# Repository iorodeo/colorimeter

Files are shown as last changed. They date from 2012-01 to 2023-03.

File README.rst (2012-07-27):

Colorimeter
-----------

Design files, software and firmware for IO Rodeos's open source (hardware &
software) scientific colorimeter kit for educators, students and DIY
scientists. Colorimeters are analytical devices commonly used in science labs to measure
the concentration of a solution from its light absorbing properties.
Colorimeters are extremely useful and flexible lab instruments for a wide range
of science education labs. 

This packages contains:

* Design files for the colorimeter Electronic Kicad) and Mechanical (py2scad) components.

* Arduino firmware and Python serial library for communicating the colorimeter.  

* A suite of software (w/GUI) for taking measurements with the colorimeter - e.g. 
  measuring transmittance and absorbance, generating standard curves, and  measuring 
  the concentration of solutions.

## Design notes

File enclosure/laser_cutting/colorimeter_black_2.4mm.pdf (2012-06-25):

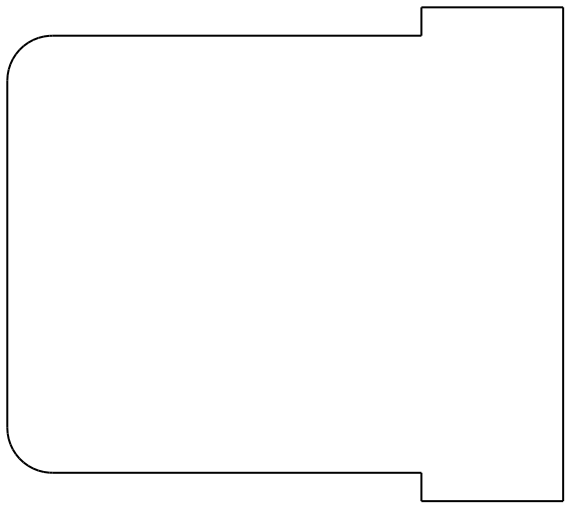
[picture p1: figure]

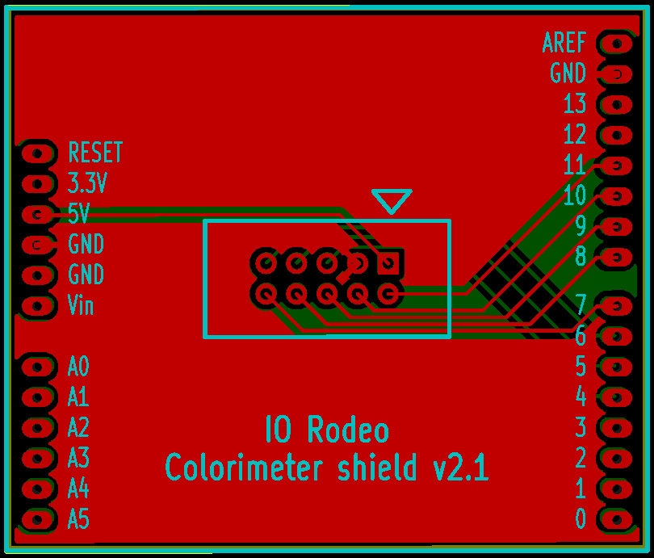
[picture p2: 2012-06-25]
kicad_design/colorimeter_shield/gerber_shield_v2p1/colorimeter_shield.png

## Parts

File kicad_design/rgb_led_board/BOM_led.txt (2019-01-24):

part        decription                        vendor      PN                               QTY
----------------------------------------------------------------------------------------------------
U1          SMT RGB LED                       Digikey    475-2822-1-ND or 475-3547-1-ND     1
P1          4 pin SMT male header             Digikey    S1013E-04-ND                       1
R1, R2      SMT resistor 90 ohm               Digikey    P90.9CCT-ND                        2
R3          SMT resistor 150 ohm              Digikey    P150CCT-ND                         1

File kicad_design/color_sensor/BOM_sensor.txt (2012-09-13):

part     decription                        vendor   PN                  QTY
----------------------------------------------------------------------------------
U1      SMT Color sensor	               Mouser	856-TCS3200D-TR       1
P2      4 pin SMT male header              Digikey	S1013E-04-ND          1
C1      SMT 0.1uF capacitor	               Digikey	490-1577-1-ND         1
P1      5x2 shrouded header	               Digikey	S9169-ND              1

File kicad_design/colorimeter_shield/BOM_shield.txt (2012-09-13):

part     decription                        vendor   PN                  QTY
----------------------------------------------------------------------------------
P1       5x2 shrouded header	           Digikey	S9169-ND             1
P2       0.1" breakaway male pin header    Digikey  SAM1031-30-ND        1

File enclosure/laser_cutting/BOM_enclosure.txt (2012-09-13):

QTY      decription                          vendor          PN                  
------------------------------------------------------------------------
4        4-40 hex standoffs 1 ¾” long        McMaster-Carr   91780A038
2        4-40 hex standoffs 1 ¼” long        McMaster-Carr   91780A034
16       4-40 machine screws 3/8” long       McMaster-Carr   91249A108
4        4-40 machine screws 1/2" long       McMaster-Carr   91249A111
8        4-40 machine screw nuts             McMaster-Carr   96537A120
4        3” female-female wire               Pololu          1806
2        connector housing                   Pololu          1903

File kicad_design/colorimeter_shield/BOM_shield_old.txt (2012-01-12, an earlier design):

part     decription                        vendor   PN                  QTY
----------------------------------------------------------------------------------
C1       SMT 10uF Capacitor 	           Digikey	493-2886-1-ND        1
P1       4x1 connector – friction lock	   Digikey	A1922-ND             1
P2       5x2 shrouded header	           Digikey	S9169-ND             1
P4       2-pin connector		
K1       3-pin connector		
SW1      SMT switch	                       Digikey	CKN10223CT-ND        1
RV1      Potentiometer	                   Digikey	CT2264-ND            1
SHIELD1  Arduino Stackable Header Kit 	   Sparkfun	PRT-10007            1

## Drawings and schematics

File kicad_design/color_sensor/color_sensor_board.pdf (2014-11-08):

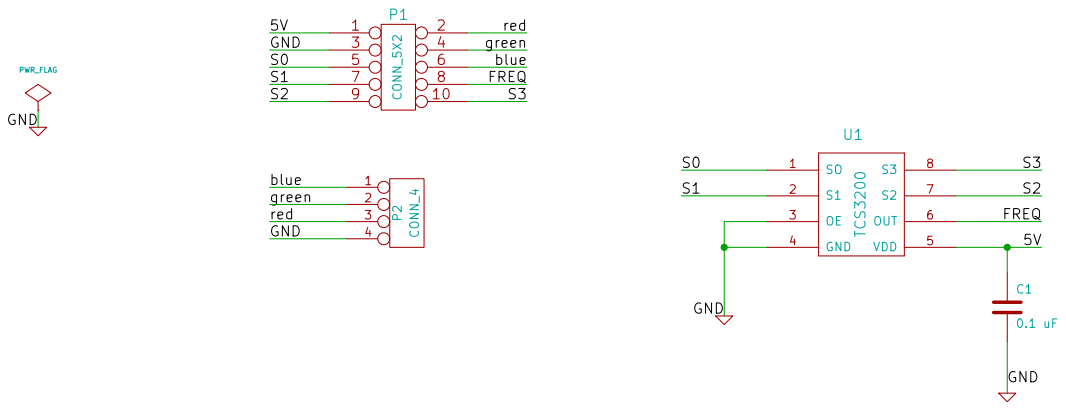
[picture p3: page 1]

Id: 1/1 Title: File: color_sensor_board.sch
Sheet: /

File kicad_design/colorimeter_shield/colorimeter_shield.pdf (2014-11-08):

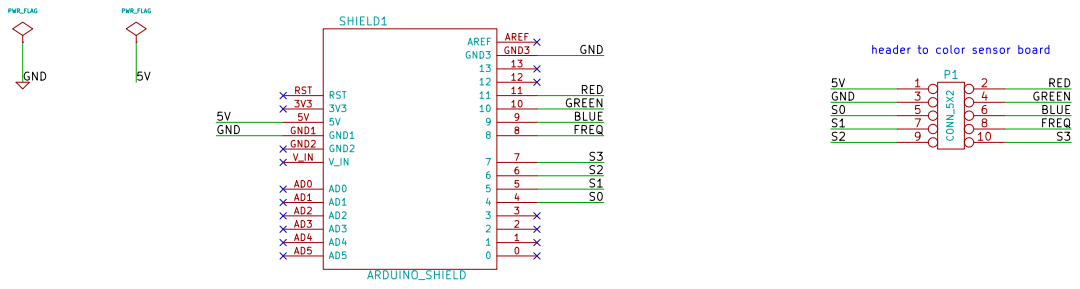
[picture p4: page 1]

9 BLUE
8 | FREQ

Id: 1/1 Title: File: colorimeter_shield.sch
Sheet: /

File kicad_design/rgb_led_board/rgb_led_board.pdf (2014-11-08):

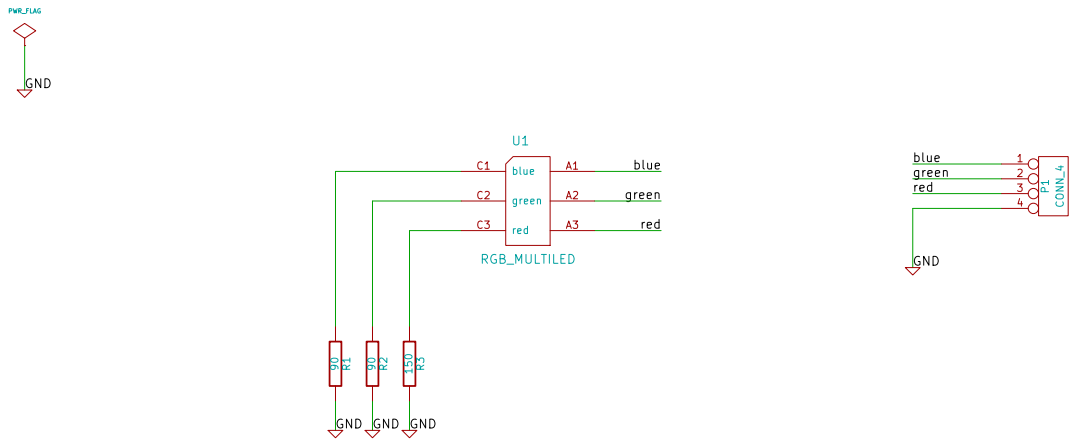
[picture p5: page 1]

Id: 1/1 Title: File: rgb_led_board.sch
Sheet: /

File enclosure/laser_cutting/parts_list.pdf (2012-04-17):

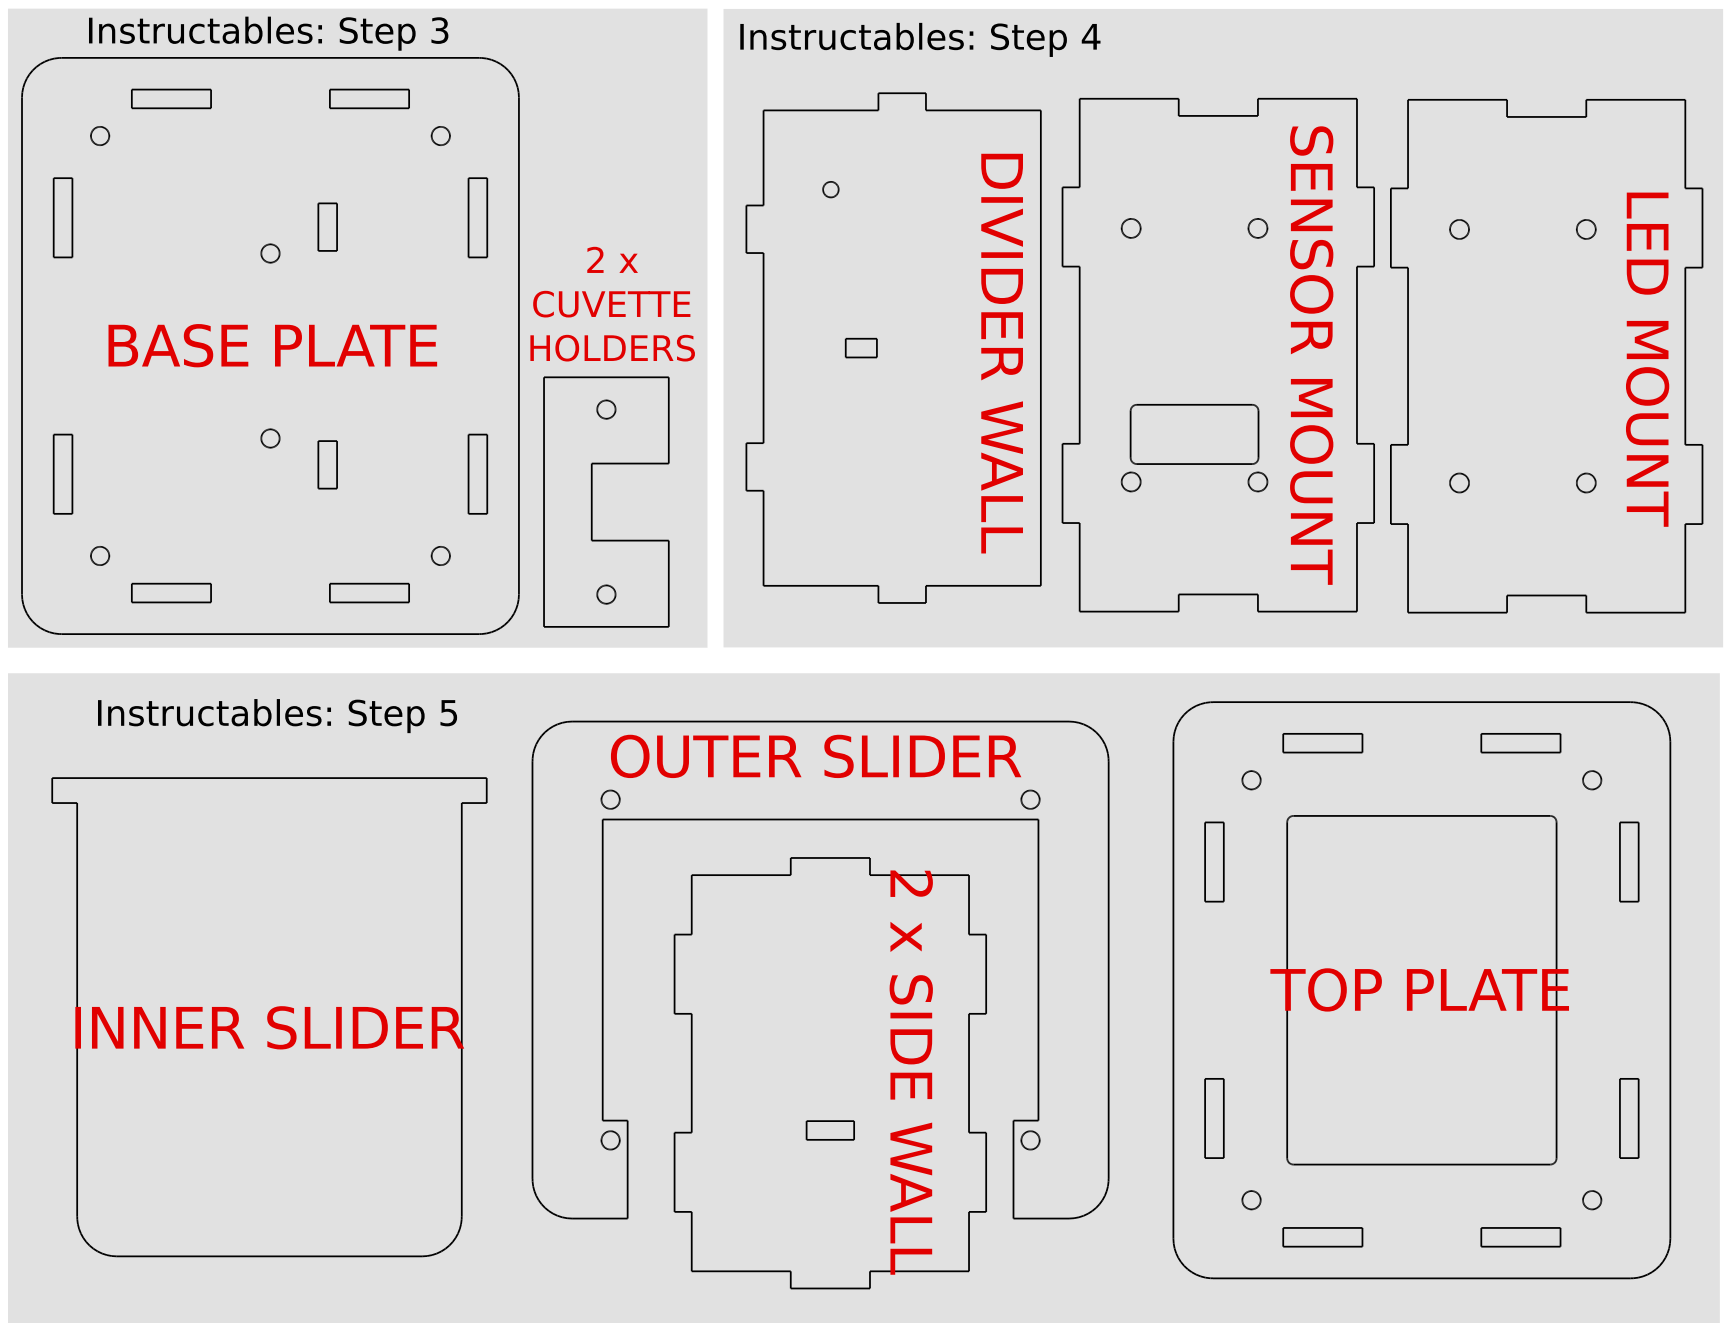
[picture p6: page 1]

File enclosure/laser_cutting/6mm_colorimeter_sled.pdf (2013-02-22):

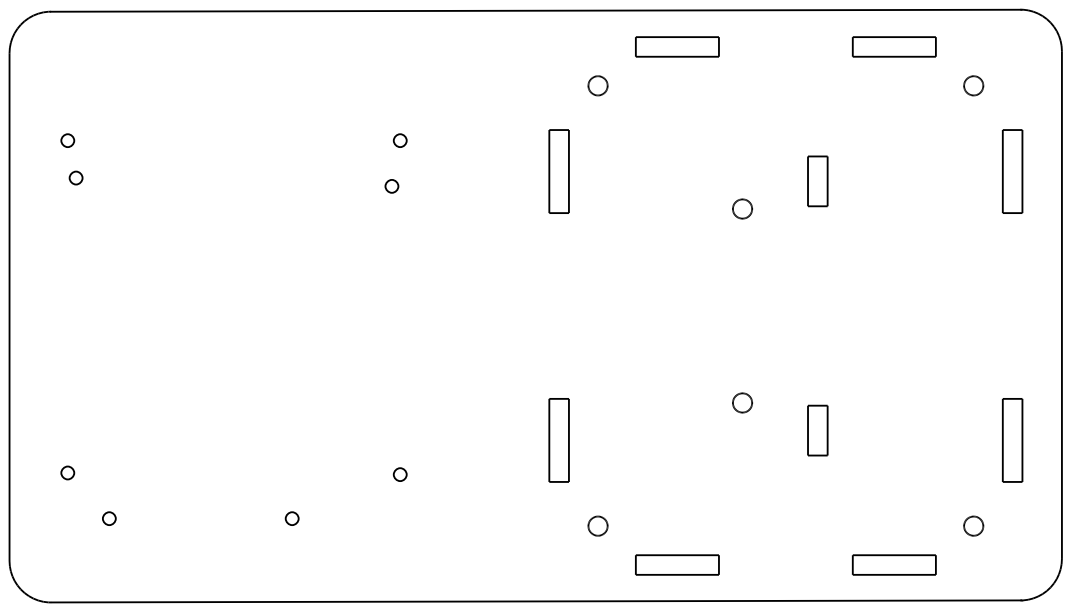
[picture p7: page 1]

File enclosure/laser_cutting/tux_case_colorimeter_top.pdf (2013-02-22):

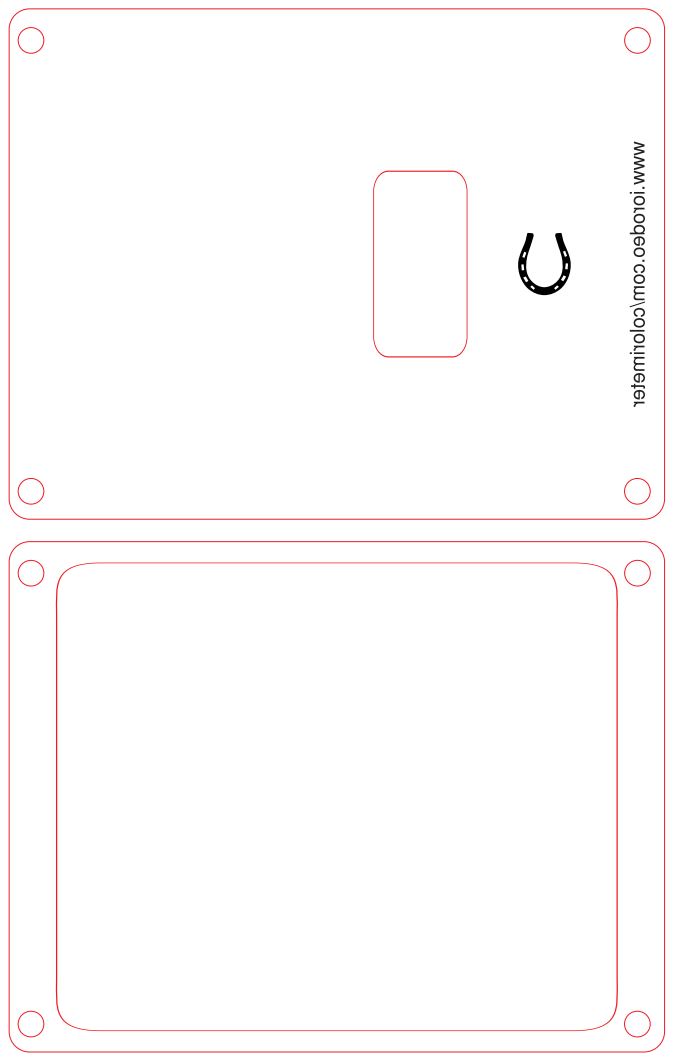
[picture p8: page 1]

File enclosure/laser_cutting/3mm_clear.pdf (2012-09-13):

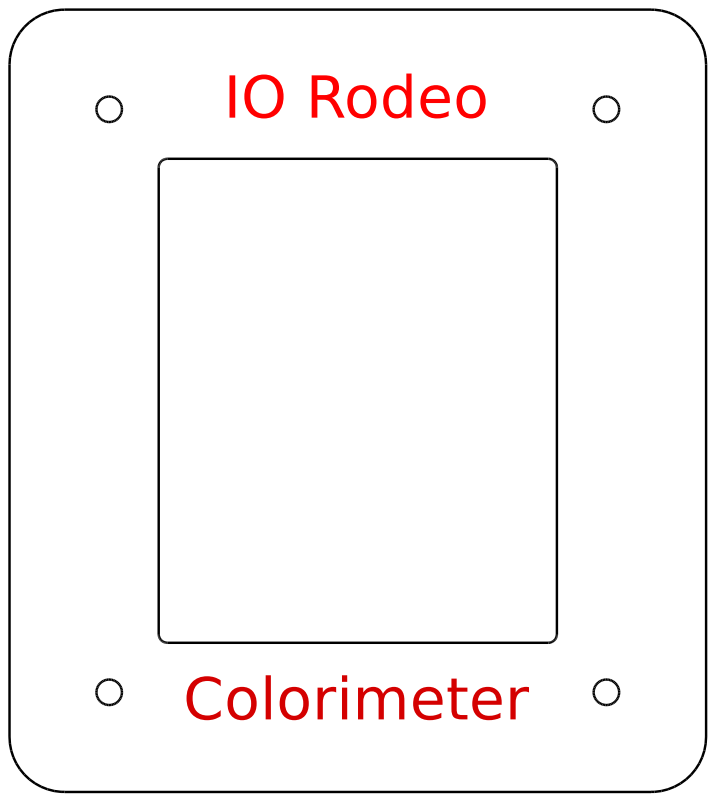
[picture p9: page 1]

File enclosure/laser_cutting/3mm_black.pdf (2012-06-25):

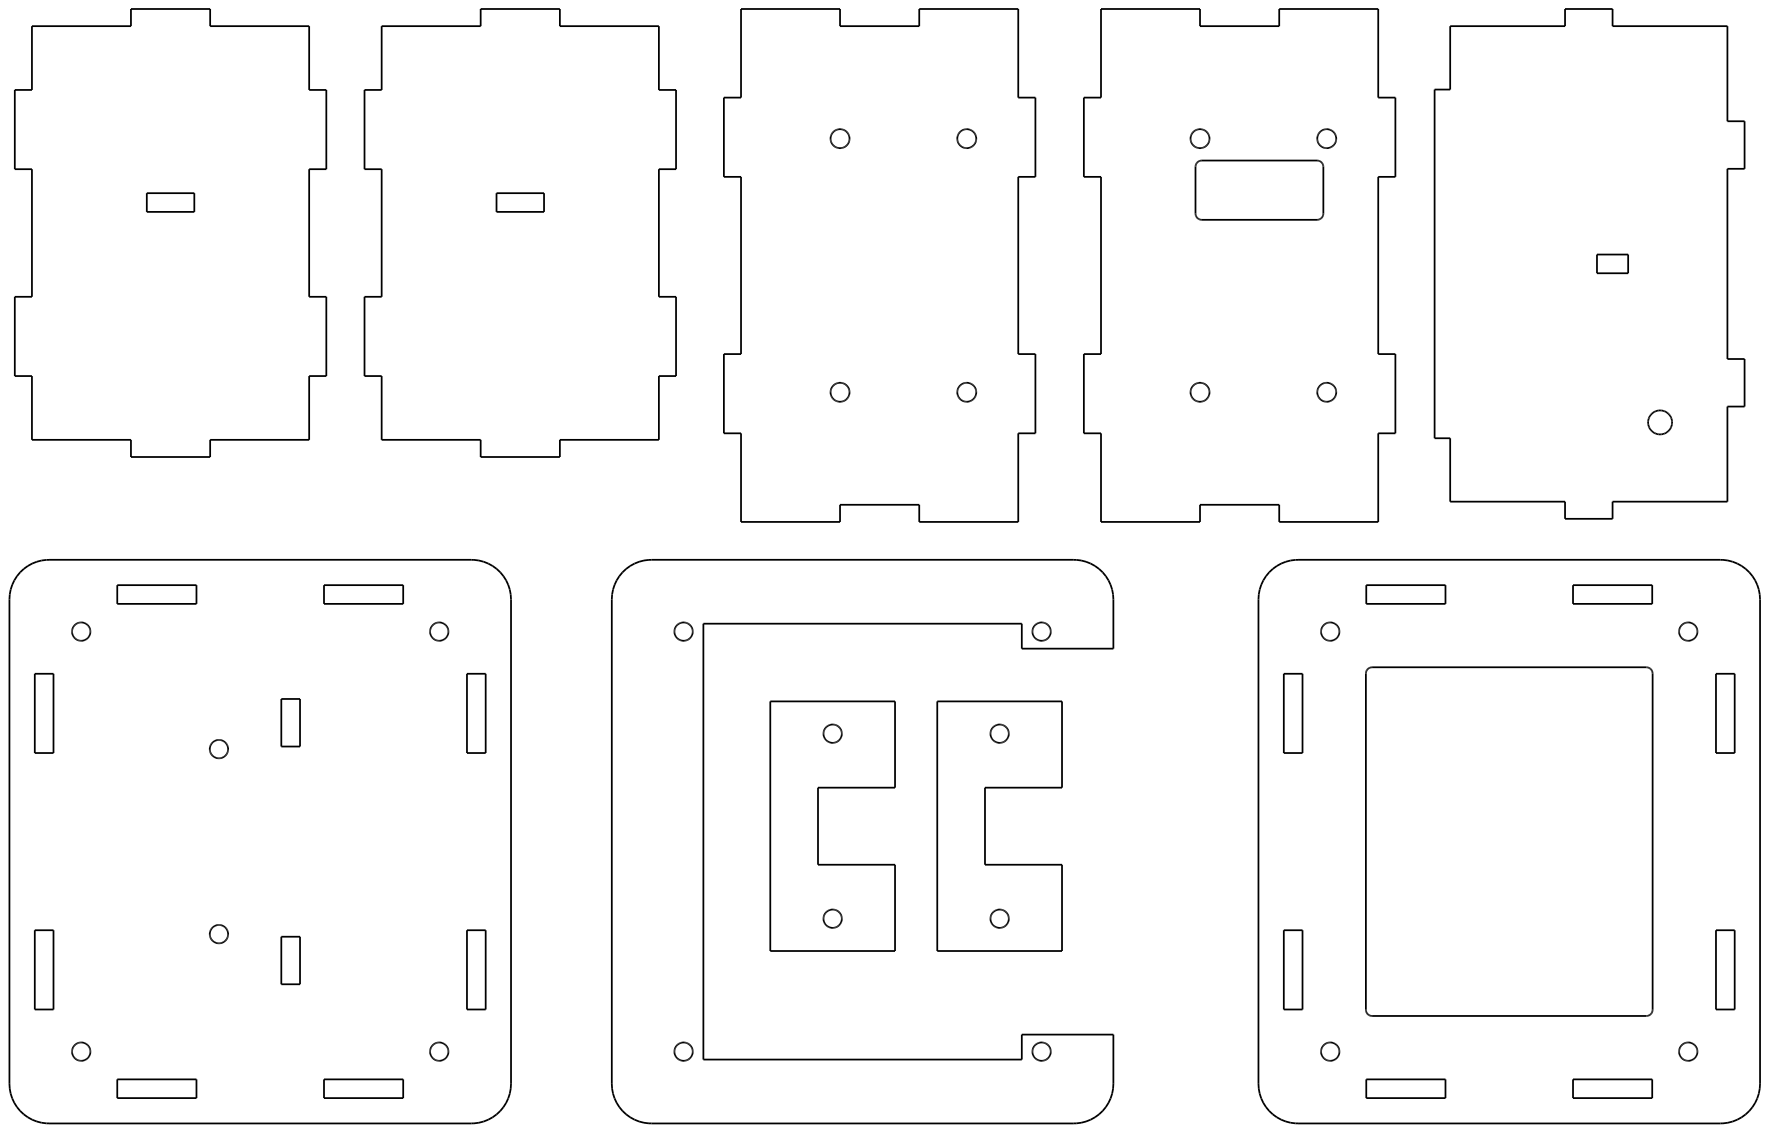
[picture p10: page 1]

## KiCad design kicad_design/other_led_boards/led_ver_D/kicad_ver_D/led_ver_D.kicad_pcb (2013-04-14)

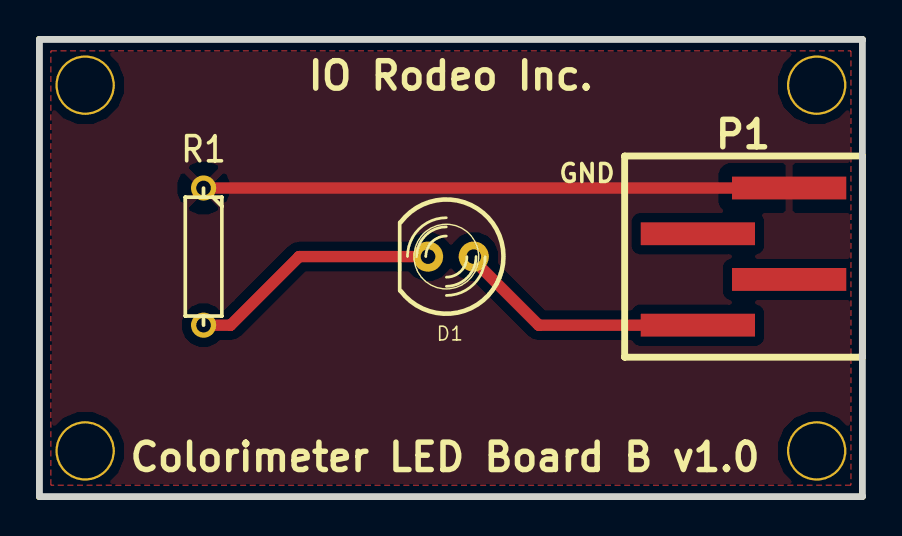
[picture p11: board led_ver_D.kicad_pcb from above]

Board: 2 copper layers, 45.7 x 25.4 mm, 7 parts (0 on the bottom side), 3 nets.

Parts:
D1: LED; LED-5MM
M1, M2, M3, M4: MOUNT_HOLE_4_40
P1: CONN_4; smt
R1: 40; R3

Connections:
/Blue: D1.1, P1.1
GND: P1.4, R1.1
unnamed: D1.2, R1.2

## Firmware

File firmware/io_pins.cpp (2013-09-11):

#include "io_pins.h"
#if defined(ARDUINO) && ARDUINO >= 100
#include "Arduino.h"
#else
#include "WProgram.h"
#endif

#ifndef BLE_SHIELD

// IO Pins for UNO Shield 
// --------------------------------------------------------

// RGB LED Control Pins
const int LED_BLU_PIN = 9; 
const int LED_GRN_PIN = 10; 
const int LED_RED_PIN = 11;

// Color Sensor Control Pins
const int COLOR_SENSOR_S0 = 4; 
const int COLOR_SENSOR_S1 = 5; 
const int COLOR_SENSOR_S2 = 6; 
const int COLOR_SENSOR_S3 = 7; 
const int COLOR_SENSOR_FO = 8;       

#else

// IO Pins for BLE shield
// --------------------------------------------------------

// RGB LED Control Pins
const int LED_BLU_PIN = 3; 
const int LED_GRN_PIN = A1; 
const int LED_RED_PIN = A0;

// Color Sensor Control Pins
const int COLOR_SENSOR_S0 = 4; 
const int COLOR_SENSOR_S1 = 5; 
const int COLOR_SENSOR_S2 = 6; 
const int COLOR_SENSOR_S3 = 7; 
const int COLOR_SENSOR_FO = 2;       

#endif

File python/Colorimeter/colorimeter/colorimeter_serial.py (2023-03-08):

from __future__ import print_function
import serial
import time

RESET_SLEEP_T = 2.0

CMD_CALIBRATE = 0
CMD_GET_MEASUREMENT = 1
CMD_SET_NUM_SAMPLES = 2
CMD_GET_NUM_SAMPLES = 3
CMD_GET_CALIBRATION = 4

CMD_CALIBRATE_RED = 5 
CMD_CALIBRATE_GREEN = 6
CMD_CALIBRATE_BLUE = 7
CMD_CALIBRATE_WHITE = 8

CMD_GET_MEASUREMENT_RED = 9
CMD_GET_MEASUREMENT_GREEN = 10
CMD_GET_MEASUREMENT_BLUE = 11
CMD_GET_MEASUREMENT_WHITE = 12

CMD_SET_MODE_COLOR_SPECIFIC = 13
CMD_SET_MODE_COLOR_INDEPENDENT = 14
CMD_GET_SENSOR_MODE = 15

SENSOR_MODE_COLOR_SPECIFIC = 0
SENSOR_MODE_COLOR_INDEPENDENT = 1

LED_COLOR_LIST = 'red', 'green', 'blue', 'white'

RSP_ERROR = 0
RSP_SUCCESS = 1

class Colorimeter(serial.Serial):

    def __init__(self, port, timeout=10.0, debug=False):
        params = {'baudrate': 9600, 'timeout': timeout}
        super(Colorimeter,self).__init__(port,**params)
        time.sleep(RESET_SLEEP_T)
        self.debug=debug
        self.clearBuffer()

    def clearBuffer(self):
        time.sleep(0.1)
        while self.inWaiting() > 0:
            self.read(self.inWaiting())
            time.sleep(0.1)

    def sendCmd(self,cmd):
        """
        Send command to colorimeter and receiver response.
        """
        self.write('{0}\n'.format(cmd).encode())
        rsp = self.readline()
        self.clearBuffer()
        if self.debug:
            print('cmd: ', cmd)
            print('rsp: ', rsp)

        if len(rsp) < 2:
            raise IOError('response from device is too short')

        if rsp[1] == str(RSP_ERROR):
            raise IOError('RSP_ERROR: {0}'.format(rsp))

        try:
            rsp = eval(rsp.strip())
        except Exception:
            raise IOError('bad response unable to parse result')

        return rsp
        
    def calibrate(self,color=None):
        """
        Calibrate the colorimeter (all channels).
        """
        if color is None:
            cmd = '[{0}]'.format(CMD_CALIBRATE) 
            rsp = self.sendCmd(cmd)
        else:
            color = color.lower()
            if not color in LED_COLOR_LIST:
                raise ValueError('unknown device color {0}'.format(color))
            calFunc = getattr(self,'calibrate{0}'.format(color.title()))
            rsp = calFunc()

    def calibrateRed(self):
        """
        Calibrate the red channel of the colorimeter
        """
        cmd = '[{0}]'.format(CMD_CALIBRATE_RED)
        rsp = self.sendCmd(cmd)

    def calibrateGreen(self):
        """
        Calibrate the green channel of the colorimeter
        """
        cmd = '[{0}]'.format(CMD_CALIBRATE_GREEN)
        rsp = self.sendCmd(cmd)

    def calibrateBlue(self):
        """
        Calibrate the blue channe of the colorimeter
        """
        cmd = '[{0}]'.format(CMD_CALIBRATE_BLUE)
        rsp = self.sendCmd(cmd)

    def calibrateWhite(self):
        """
        Calibrate the white channel of the colorimeter
        """
        cmd = '[{0}]'.format(CMD_CALIBRATE_WHITE)
        rsp = self.sendCmd(cmd)

    def getCalibration(self):
        """
        Get the current calibration freqeuncy values.

        Returns the calibration freqeuncies for red, green, blue and white
        light.
        """
        cmd = '[{0}]'.format(CMD_GET_CALIBRATION)
        rsp = self.sendCmd(cmd)
        return rsp[1:5] 

    def getMeasurement(self,color='all'):
        """
        Get a measurement from the device. 
        """
        if color == 'all':
            cmd = '[{0}]'.format(CMD_GET_MEASUREMENT)
            rsp = self.sendCmd(cmd)
            freq = tuple(rsp[1:5])
            tran = tuple(rsp[5:9])
            abso = tuple(rsp[9:])
        elif color in ('red', 'green', 'blue', 'white'):
            measureFunc = getattr(self,'getMeasurement{0}'.format(color.title()))
            freq, tran, abso = measureFunc()
        else:
            raise ValueError('unknown color {0}'.format(color))
        return freq, tran, abso

    def getMeasurementRed(self):
        """
        Get a measurement from the red channel
        """
        cmd = '[{0}]'.format(CMD_GET_MEASUREMENT_RED)
        rsp = self.sendCmd(cmd)
        freq, tran, abso = rsp[1:4]
        return freq, tran, abso

    def getMeasurementGreen(self):
        """
        Get a measurement from the green channel
        """
        cmd = '[{0}]'.format(CMD_GET_MEASUREMENT_GREEN)
        rsp = self.sendCmd(cmd)
        freq, tran, abso = rsp[1:4]
        return freq, tran, abso

    def getMeasurementBlue(self):
        """
        Get a measurement from the blue channel
        """
        cmd = '[{0}]'.format(CMD_GET_MEASUREMENT_BLUE)
        rsp = self.sendCmd(cmd)
        freq, tran, abso = rsp[1:4]
        return freq, tran, abso

    def getMeasurementWhite(self):
        """
        Get a measurement from the white channel
        """
        cmd = '[{0}]'.format(CMD_GET_MEASUREMENT_WHITE)
        rsp = self.sendCmd(cmd)
        freq, tran, abso = rsp[1:4]
        return freq, tran, abso

    def setNumSamples(self,value):
        """
        Set the number of samples aquired per measurement.
        """
        if value <= 0 or value > (2**16-1):
            raise ValueError('numSamples must be > 0 or < 2**16 -1')
        cmd = '[{0}, {1}]'.format(CMD_SET_NUM_SAMPLES,value)
        rsp = self.sendCmd(cmd)

    def getNumSamples(self):
        """
        Get the current value set for the number of samples per measurement.
        """
        cmd = '[{0}]'.format(CMD_GET_NUM_SAMPLES) 
        rsp = self.sendCmd(cmd)
        numSamples = rsp[1]
        return numSamples

    def setSensorModeColorSpecific(self):
        """
        Set the sensor to color specific mode. In this mode it will use the 
        red/green/blue/clear color channel of the sensor when using the 
        red/green/blue/white led.
        """
        cmd = '[{0}]'.format(CMD_SET_MODE_COLOR_SPECIFIC)
        rsp = self.sendCmd(cmd)

    def setSensorModeColorIndependent(self):
        """
        Set the sensor to color independent mode. In this mode the clear
        (unfiltered) channel of the light sensor is used regardless of the led
        selected.
        """
        cmd = '[{0}]'.format(CMD_SET_MODE_COLOR_INDEPENDENT)
        rsp = self.sendCmd(cmd)

    def getSensorMode(self):
        """
        Returns the current color sensor mode setting.
        """
        cmd = '[{0}]'.format(CMD_GET_SENSOR_MODE)
        rsp = self.sendCmd(cmd)
        sensorMode = rsp[1]
        return sensorMode

    def printMeasurement(self):
        """
        Test function. Gets a measurement and pretty prints it.
        """
        f, t, a = self.getMeasurement()

        print('Frequency:')
        print('  red:    {0:1.2f}'.format(f[0]))
        print('  green:  {0:1.2f}'.format(f[1]))
        print('  blue:   {0:1.2f}'.format(f[2]))
        print('  white:  {0:1.2f}'.format(f[3]))

        print('Transmission:')
        print('  red:    {0:1.2f}'.format(t[0]))
        print('  green:  {0:1.2f}'.format(t[1]))
        print('  blue:   {0:1.2f}'.format(t[2]))
        print('  white:  {0:1.2f}'.format(t[3]))

        print('Absorbance:')
        print('  red:    {0:1.2f}'.format(a[0]))
        print('  green:  {0:1.2f}'.format(a[1]))
        print('  blue:   {0:1.2f}'.format(a[2]))
        print('  white:  {0:1.2f}'.format(a[3]))

# -----------------------------------------------------------------------------
if __name__ == '__main__':

    dev = Colorimeter('/dev/ttyACM0')
    dev.printMeasurement()







    
        

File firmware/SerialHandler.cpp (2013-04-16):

#if defined(ARDUINO) && ARDUINO >= 100
#include "Arduino.h"
#else
#include "WProgram.h"
#endif
#include "SerialHandler.h"
#include "Streaming.h"

// Constants
// ----------------------------------------------------------------------------
const int CMD_CALIBRATE=0;
const int CMD_GET_MEASUREMENT=1;
const int CMD_SET_NUM_SAMPLES=2;
const int CMD_GET_NUM_SAMPLES=3;
const int CMD_GET_CALIBRATION=4;

const int CMD_CALIBRATE_RED=5;
const int CMD_CALIBRATE_GREEN=6;
const int CMD_CALIBRATE_BLUE=7;
const int CMD_CALIBRATE_WHITE=8;

const int CMD_GET_MEASUREMENT_RED=9;
const int CMD_GET_MEASUREMENT_GREEN=10;
const int CMD_GET_MEASUREMENT_BLUE=11;
const int CMD_GET_MEASUREMENT_WHITE=12;

const int CMD_SET_MODE_COLOR_SPECIFIC=13;
const int CMD_SET_MODE_COLOR_INDEPENDENT=14;
const int CMD_GET_SENSOR_MODE = 15;

const int RSP_ERROR = 0;
const int RSP_SUCCESS = 1;

const uint8_t DBL_STR_LEN = 30;
const uint8_t DBL_PREC = 12;



// Methods
// ----------------------------------------------------------------------------
void SerialHandler::processInput() { 
    while (Serial.available() > 0) {
        process(Serial.read());
        if (messageReady()) {
            switchYard();
            reset();
        }
    }
}

void SerialHandler::switchYard() { 
    uint8_t cmdId;

    cmdId = readInt(0); 

    switch (cmdId) {

        case CMD_CALIBRATE:
            calibrate();
            break;

        case CMD_GET_MEASUREMENT:
            sendMeasurement();
            break;

        case CMD_SET_NUM_SAMPLES:
            setNumSamples();
            break;

        case CMD_GET_NUM_SAMPLES:
            sendNumSamples();
            break;

        case CMD_GET_CALIBRATION:
            sendCalibration();
            break;

        case CMD_CALIBRATE_RED:
            calibrateRed();
            break;

        case CMD_CALIBRATE_GREEN:
            calibrateGreen();
            break;

        case CMD_CALIBRATE_BLUE:
            calibrateBlue();
            break;

        case CMD_CALIBRATE_WHITE:
            calibrateWhite();
            break;

        case CMD_GET_MEASUREMENT_RED:
            sendMeasurementRed();
            break;

        case CMD_GET_MEASUREMENT_GREEN:
            sendMeasurementGreen();
            break;

        case CMD_GET_MEASUREMENT_BLUE:
            sendMeasurementBlue();
            break;

        case CMD_GET_MEASUREMENT_WHITE:
            sendMeasurementWhite();
            break;

        case CMD_SET_MODE_COLOR_SPECIFIC:
            setModeColorSpecific();
            break;

        case CMD_SET_MODE_COLOR_INDEPENDENT:
            setModeColorIndependent();
            break;

        case CMD_GET_SENSOR_MODE:
            sendSensorMode();
            break;

        default:
            unknownCmd();
            break;
    }
}

void SerialHandler::calibrate() { 
    colorimeter.calibrate();
    if (colorimeter.checkCalibration() ) {
        colorimeter.EEPROM_saveCalibration();
        Serial << '[' << RSP_SUCCESS << ']' << endl;
    } 
    else {
        Serial << '[' << RSP_ERROR; 
        Serial << ',' << "calibration failed";
        Serial << ']' << endl;
    }
}

void SerialHandler::calibrateRed() {
    colorimeter.calibrateRed();
    if (colorimeter.checkCalibrationRed()) {
        colorimeter.EEPROM_saveCalibrationRed();
        Serial << '[' << RSP_SUCCESS << ']' << endl;
    }
    else {
        Serial << '[' << RSP_ERROR; 
        Serial << ',' << "calibration failed";
        Serial << ']' << endl;
    }
}

void SerialHandler::calibrateGreen() {
    colorimeter.calibrateGreen();
    if (colorimeter.checkCalibrationGreen()) {
        colorimeter.EEPROM_saveCalibrationGreen();
        Serial << '[' << RSP_SUCCESS << ']' << endl;
    }
    else {
        Serial << '[' << RSP_ERROR; 
        Serial << ',' << "calibration failed";
        Serial << ']' << endl;
    }
}

void SerialHandler::calibrateBlue() {
    colorimeter.calibrateBlue();
    if (colorimeter.checkCalibrationBlue()) {
        colorimeter.EEPROM_saveCalibrationBlue();
        Serial << '[' << RSP_SUCCESS << ']' << endl;
    }
    else {
        Serial << '[' << RSP_ERROR; 
        Serial << ',' << "calibration failed";
        Serial << ']' << endl;
    }
}

void SerialHandler::calibrateWhite() {
    colorimeter.calibrateWhite();
    if (colorimeter.checkCalibrationWhite()) {
        colorimeter.EEPROM_saveCalibrationWhite();
        Serial << '[' << RSP_SUCCESS << ']' << endl;
    }
    else {
        Serial << '[' << RSP_ERROR; 
        Serial << ',' << "calibration failed";
        Serial << ']' << endl;
    }
}

void SerialHandler::sendMeasurement() { 
    char valueStr[DBL_STR_LEN];

    colorimeter.getMeasurement();

    Serial << '[' << RSP_SUCCESS;
    Serial << ',' << _DEC(colorimeter.frequency.red);
    Serial << ',' << _DEC(colorimeter.frequency.green);
    Serial << ',' << _DEC(colorimeter.frequency.blue);
    Serial << ',' << _DEC(colorimeter.frequency.white);

    dtostre(colorimeter.transmission.red, valueStr, DBL_PREC, 0);
    Serial << ',' << valueStr;
    dtostre(colorimeter.transmission.green, valueStr, DBL_PREC, 0);
    Serial << ',' << valueStr;
    dtostre(colorimeter.transmission.blue, valueStr, DBL_PREC, 0);
    Serial << ',' << valueStr;
    dtostre(colorimeter.transmission.white, valueStr, DBL_PREC, 0);
    Serial << ',' << valueStr;

    dtostre(colorimeter.absorbance.red, valueStr, DBL_PREC, 0);
    Serial << ',' << valueStr;
    dtostre(colorimeter.absorbance.green, valueStr, DBL_PREC, 0);
    Serial << ',' << valueStr;
    dtostre(colorimeter.absorbance.blue, valueStr, DBL_PREC, 0);
    Serial << ',' << valueStr;
    dtostre(colorimeter.absorbance.white, valueStr, DBL_PREC, 0);
    Serial << ',' << valueStr;
    Serial << ']' << endl;
}

void SerialHandler::setNumSamples() {
    long numSamples;
    numSamples = readLong(1);
    if ((numSamples > 0) && (numSamples <= 65535)) {
        colorimeter.numSamples = (uint16_t) numSamples;
        Serial << '[' << RSP_SUCCESS << ']' << endl;
    }
    else {
        Serial << '[' << RSP_ERROR; 
        Serial << ',' << "out of range";
        Serial << ']' << endl;
    }
} 

void SerialHandler::sendNumSamples() {
    Serial << '[' << RSP_SUCCESS;
    Serial << ',' << _DEC(colorimeter.numSamples);
    Serial << ']' << endl;
}
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

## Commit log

2011-12-31 Project creation.
    [color_sensor_board-Back.gbl, color_sensor_board-Front.gtl, color_sensor_board-Mask_Back.gbs, color_sensor_board-Mask_Front.gts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]
2012-01-04 New rgb led design.
    [$savepcb.brd, rgb_led_board.brd, rgb_led_board.dsn, rgb_led_board.sch]
2012-01-05 Added Kicad design for the Arduino shield for the colorimeter.
    [$savepcb.brd, colorimeter_shield.brd, colorimeter_shield.sch]
2012-01-07 Added KiCad footprints for two surface mount components.
    [$savepcb.brd, colorimeter_shield.brd]
2012-01-10 Finished designing Arduino shield PCB for the colorimeter.
    [$savepcb.brd, colorimeter_shield.brd, colorimeter_shield.dsn, colorimeter_shield.sch]
2012-01-11 Created new version 1.1 of the color sensor PCB. New version has a 5x2 header replacing the 6x2 header. Routed the shield board and re-routed sensor v1.1. Created gerber files.
    [$savepcb.brd, color_sensor_board-Back.gbl, color_sensor_board-Front.gtl, color_sensor_board-Mask_Back.gbs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]
2012-01-12 Added BOMs for all three boards.
2012-01-14 Enclosure changes - resized holes and added cuvette holder.
2012-01-17 Worked on the enclosure designs. Started to add in the new sliding cover.
2012-01-18 Worked on py2scad enclosure design.
2012-01-19 Finished version 2 of the new colorimenter enclosure design.
2012-01-20 Finished writing absorbance calculation. Next up calibration.
2012-02-03 Finished serial interface - both for firmware and host. Wrote a simple gui for working with the device.
2012-02-03 Added IO pins for arduino uno shield.
2012-02-07 Fixed bug in firmware which caused white values to be the same as the red values. Added color selection checkboxes to GUI. Added number of samples line edit to GUI.
2012-02-10 Changes to the sensor and LED boards to replace the terminal blocks with surface mount components.
    [$savepcb.brd, color_sensor_board.brd, color_sensor_board.sch, rgb_led_board.brd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]
2012-02-10 Version 2 of the colorimeter. Removed alot of the components that are not necessary to make a very basic breakout board.
    [$savepcb.brd, colorimeter_shield.brd, colorimeter_shield.dsn, colorimeter_shield.sch]
2012-02-10 version 2p0 gerber files for sensor, led and shield boards.
    [$savepcb.brd, color_sensor_board.brd, color_sensor_board.dsn, colorimeter_shield.brd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]
2012-02-11 New project: Nano colorimeter shield
    [$savepcb.brd, color_sensor_board-Back.gbl, color_sensor_board-Front.gtl, color_sensor_board-Mask_Back.gbs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]
2012-02-15 Fixed design bugs. Still need to remake dxf files, etc.
    [color_sensor_board-Front.gtl]
2012-03-03 Modified both sensor and LED boards to a new surface mount 4-pin male header instead of the poke home connectors. New gerber files v2p1 for both boards.
    [$savepcb.brd, color_sensor_board-Back.gbl, color_sensor_board-Front.gtl, color_sensor_board-Mask_Back.gbs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]
2012-03-21 Added an annotated parts list for the enclosure.
2012-04-10 Added prototype of colorimater plotting GUI.
2012-05-30 Created slight offset in shrouded header hole position for sensor pcb.
2012-05-30 Modified inner panel slot position so that it is better aligned with the led and sensor.
2012-06-25 Added silk screen markings to the arduino sheild. Changed the silk screen marking on the LED board - modified version number.
    [$savepcb.brd, colorimeter_shield-Back.gbl, colorimeter_shield-Front.gtl, colorimeter_shield-Mask_Back.gbs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]
2012-06-25 Modified inner panel LED cable hole size. Remade laser cutting files. Restructured project file slightly.
2012-07-07 Worked on measurement GUI plotting. Added live updating of plot - to new measurements and update of sample labels. Added computation of test solution coefficients from data files. Worked on delete fu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
2012-07-16 Added led to data saved by plot and measurement GUI. LED is also now set when data is loaded into the plot GUI.
2012-07-20 Worked on basic program. Fixed some issues with bar chart as it didn't reflect the current led selection. Made it so that bar chart updates with any changes to GUI and closes when GUI is closed.
2012-07-24 Further work on unify the basic program with the other two - plotting and measurement. Some minor changes to the device firmware.
2012-07-24 Fixed some issues with how GUIs handle calibration failures.
2012-09-13 Cleaned up laser cutting files.
2012-09-13 Added BOMs and clean up laser cutting files.
2012-12-20 Added method to color sensor class to allow selecting the sensors frequency scaling. Changed the default frequency scaling from 20% to 100% to enable measurement of higher concentrations. Set python 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
2012-12-21 Added copy of pyinstaller .spec file for compiling stand alone binaries. Currently works with pyinstaller 1.5 haven't tested upgrade to pyinstaller 2.0.
    Added cheap hack to deal with missing item from hiddenimports in scipy hook when
    using pyinstaller.
2012-12-21 Add error dialog to measurement program for the case where the users is using a nonlinear fit and the measurement falls outside of the calibration range - basically disallow extrapolation.
2013-02-22 Added inkscape files for sled and tuxcase top.
    [rgb_led_board.sch]
2013-04-14 Added Kicad design files for additional LED boards. Version B (single LED) and Version C (two LEDs).
    [$savepcb.brd, led_ver_B.brd, led_ver_B.dsn, led_ver_B.kicad_pcb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]
2013-04-16 Worked on added ability to handle custom single LED PCB. Updateded firmware, serial libraray, and worked on updating GUI. Basic program has been modified, still need to finish modifiying the plotting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
2013-04-21 Worked on adding new custom LED mode to plotting and measurement programs.
2013-04-21 Finished modifications to software so that the colorimeter can be used with the 'custom' LED PCB.
2013-04-24 Changed default number of samples. Fixed bug which occured when switching to custom LED mode when there was no test solution data avialable.
2013-04-25 Added lineEdit for setting number for samples to the plot and measure programs.
2013-08-30 Began work adding modes for using both custom led board version B and C.
2013-08-31 Worked on adding custom led option for version c pcb.
2013-09-03 Worked on adding new ver C PCB mode. Refactoring how this is handled.
2013-09-11 Added pin definitions for BLE shield.
2013-10-26 Worked on additing ability to use version c pcb to plottin program. Modified GUI and made changes so that is will at least open with the new data structures.
2013-10-26 Finished modificatinos to plot.py so that it works with the version c pcb.
2013-10-27 Finished modifications to measure.py so that it will work with version c pcb.
2014-05-15 New version D design with PLCC 5050 LED and transistor switch for higher voltages. Note, still need to rename some files.
    [led_ver_B.brd, led_ver_B.dsn, led_ver_B.kicad_pcb, led_ver_B.sch]
2014-05-15 Changed some file names.
    [led_ver_D.brd, led_ver_D.dsn, led_ver_D.kicad_pcb, led_ver_D.sch]
2014-05-15 Added Gerber files for LED Ver D board.
    [led_ver_D-Back.gbl, led_ver_D-Front.gtl, led_ver_D-Mask_Back.gbs, led_ver_D-Mask_Front.gts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]
2014-07-12 Added second cuvette size.
2015-01-22 Fixed bug which caused issues with setting the default sensorMode value to anything other than StandardRGBLED.
2017-05-25 Removed LED_5050 led_5050 .bak files.
2019-01-24 Add replacement RGB LED to BOM.
